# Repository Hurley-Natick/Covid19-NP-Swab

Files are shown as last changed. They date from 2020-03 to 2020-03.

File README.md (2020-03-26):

*Last updated: March 26, 2020 1600 ET*

# Making NP swabs

As clinical laboratories around the world have begun testing for Covid-19, we have encountered a new crisis: a shortage of the swabs required to obtain the necessary sample. These are called nasopharyngeal swabs, or NP swabs for short.

**The goal of this repository is sharing [methods](#design), [testing procedures](#testing), and [results](#results) required to manufacture NP swabs locally/everywhere at volumes of thousands per day, until standard manufacturers can make and deliver more.**

Because the crisis is **now,** the goal is to re-create versions of the swabs already in use (as opposed to creating better/fundamentally different redesigns).

The files in this repo contain some information to get started. **This includes .stl files that you can modify/print (see [design_files](design_files/) above).**

If anyone has any questions, please reach out to any of the contributors here or to Dr. Ramy Arnaout, MD, DPhil, at rarnaout@bidmc.harvard.edu.

Anything you find here is free for use for all.

If you want us to test swab materials at BIDMC we are happy to, please contact Cody Callahan at BIDMC (ccallah4@bidmc.harvard.edu).

For efficiency, we strongly suggest you find local partners either in addition or instead for [testing](#testing) and ask one of [us](#contact) for write access to share your [results](#results) here on the repo.

## Summary, March 25, 2 p.m. ET

Please see [here](Results/README.md).

## Contents

- [Basic description of an NP swab](#design)
- [Requirements](#reqs)
- [Anti-requirements: What's not required](#not-reqs)
- [List of known acceptable swabs](#acceptable-swabs)
- [Manufacturing approaches](#approaches)
- [Flock](#flock)
- [Materials and adhesives](#adhesive)
- [Packaging](#packaging)
- [Testing procedures](#testing)
- [Results](#results)
- [Contact](#contact)

## Basic description of an NP swab

(Click images for larger versions)





An NP swab is a flexible stick around 15cm in length that goes up your nose to the back of the nasal cavity (see [movie](https://www.youtube.com/watch?v=hXohAo1d6tk&feature=youtu.be&t=40)). It is swept or twirled around to brush or wick up secretions, which carry Covid-19 virus particles. The swab comes out of the nose and goes into a vial that contains fluid (viral transport medium, VTM, for which there are now recipes [from IU](Other_Docs/VTM_IU_recipe.pdf) and [the CDC](Other_Docs/CDC_Viral-Transport-Medium.pdf)). The vial gets capped and sent for processing.

There are **two parts**: a bristled **bulb** end (above) and a **shaft**. The bristles in the above are nylon.

The bulb looks like it would be fluffy to the touch but it is not: the bristles are short enough that it feels more like hard foam.

Often the shaft itself has a thin **neck**, for flexibility, and a thicker **handle**. The handle is often **scored**---a weak point in the shaft---where you can break it off so the bristled part stays in the vial; the handle is then thrown away.

**Score at \~7 cm from bulb tip.** The location of the score (distance from the bulb along the handle) must be smaller than the height of the vial you use. For example, for the vials for use with Copan 480C swabs, the breakpoint is 7cm; for [15-](https://www.fishersci.com/shop/products/falcon-15ml-conical-centrifuge-tubes-5/p-193301) or [50-mL](https://www.fishersci.com/shop/products/falcon-50ml-conical-centrifuge-tubes-2/p-193321) conical tubes (of the kind used routinely in biomedical research and sold by many manufacturers), 11 cm will do. It is mildly easier for handling if the score is close to the height of the vial but the requirement is that it is less than the height.

Helpful target measurements:

- Diameter of head with bristles: 3mm
- Diameter of head without bristles: \~2mm
- Diameter of neck: 1mm
- Diameter of handle: 2.5mm
- Length of bulb: 15mm
- Length that will be submerged in [transport medium](#pcr): \~30mm

# Requirements

## Medical requirements

-	**Stiffness, flexibility.** Wand is stiff enough to push to the back of the nasal cavity but flexible enough to get up the nose and will bend when it hits resistance instead of stabbing people (for reference, swabs are a little more flexible than the tiny straws used for coffee, and somewhat similar to the inside tube that holds the ink when you take apart a Bic ballpoint pen). **Swab must not snap off in patient's nose**

-	**Tip.** Ideally, the bulb end is *flocked* (see below): it has lots of tiny bristles perpendicular to the wand (see close-up above). The bristles provide for a high surface-area-to-volume and helps both wick secretions onto the bristle and liberate particles when put in the transport medium. Perpendicularity is a nice-to-have that we believe may improve yield slightly but requires electrostatic deposition; even random orientation of flock should work fine

-	Bristles or collecting substrate (including any adhesive) must be firmly attached and not get left behind in the nasal cavity. Similarly no part of the swab should break off or get left in the nasal cavity

-	[Materials](#adhesive) cannot inhibit [PCR](https://en.wikipedia.org/wiki/Reverse_transcription_polymerase_chain_reaction). This means no wood or cotton (although we believe rayon is OK). Nylon and polypropylene seem to be good choices, but start with medical equipment/grade materials if possible since they should be high quality/pure (some additives can be inihibitors).

-	Wand must break off inside the tube – better to be too short than too long.  Wand could be manually scored to create a weak point. If not, might need scissors at point of care (not ideal)

For more technical requirements, see [Design Constraints](Other_Docs/Design%20Constraints.md)

## Anti-requirements: What's not required

-	Sterility. Not a major concern for most uses; only for immunocompromised (in which case the ability to decontaminate by [autoclaving](https://en.wikipedia.org/wiki/Autoclave) or ethanol or isopropanol bath is needed). The air and the nose are already non-sterile and the PCR assay is specific enough to ignore most contaminants (as long as other Covid-19 contaminated things/people don’t come in contact with it and it doesn’t pick up PCR inhibitors)

-	Labor intensive is ok, to fill short term needs. There are students and researchers out of school and lab who are willing to volunteer to hand-assemble these from inoculation loops, adhesive, and wicking substrate #studentArmy

## List of known acceptable swabs

Model what you make after one of these.

Product numbers are listed. Unless otherwise stated, these are from the [FDA approved list](https://www.fda.gov/medical-devices/emergency-situations-medical-devices/faqs-diagnostic-testing-sars-cov-2) current as of **March 20, 2020**. You can look these up online.

**Copan:** 480C *(2)*, 481C *(1)*, 482C *(1)*, 501CS01, 503CS01, 516CS01, 518CS01, 534CS01

**Puritan:** LA-117 *(1)*, 3317-H, 25-3317-H, 25-3316-U, 25-3316-H, 25-3317-U, 25-3318-U, 25-3318-H, 25-3319-H, 25-3320-U, 25-3320-U EMB 100MM, 25-3320-U EMB 80MM, 25-3320-H and 25-3320-H EMB 80MM

*(1)* Preferred, per FDA

*(2)* Acceptable, per BIDMC

## Manufacturing approaches

**We believe the best use of resources is to be creative around copying the template, not redesigning swabs.**

- 3D print a shaft, and attaching flock material via adhesive

- 3D print a shaft with enough definition---either "nubs" along the surface or bristles---to gather secretion from the nasopharynx.

For more detail on ideas not yet investigated, including repurposing unrelated items like cosmetics applicators, or using other items common in labs, see [Other Approaches](Other_Docs/Repurposing_Approach.md)

### 3D-print shaft + adhesive + swab

- 3D print a wand with the appropriate form factor (e.g. see the picture above and the .stl files)
- dip bulb in adhesive (we are working on appropriate adhesives)
- dip sticky bulb in [flock](#flock)
- shake/blow/rinse off excess flock
- (if needed) dip in 70% ethanol for sterilization

(This is like how you'd solve this problem if you were in elementary school.) Currently we have no proven way to automate the last three steps so we are envisioning a "student army." Better ideas welcome.

### 3D-print entire swab

The ability to print a swab complete with bristles or equivalent saves the steps for requiring adhesive and [flock](#flock).

Stereolithography 3D printed prototypes by **OPT Industries** look promising (see example bulbs, below---note in this approach the whole swab including bulb is printed at once, on their own DLP/SLA machines); we are testing materials now.

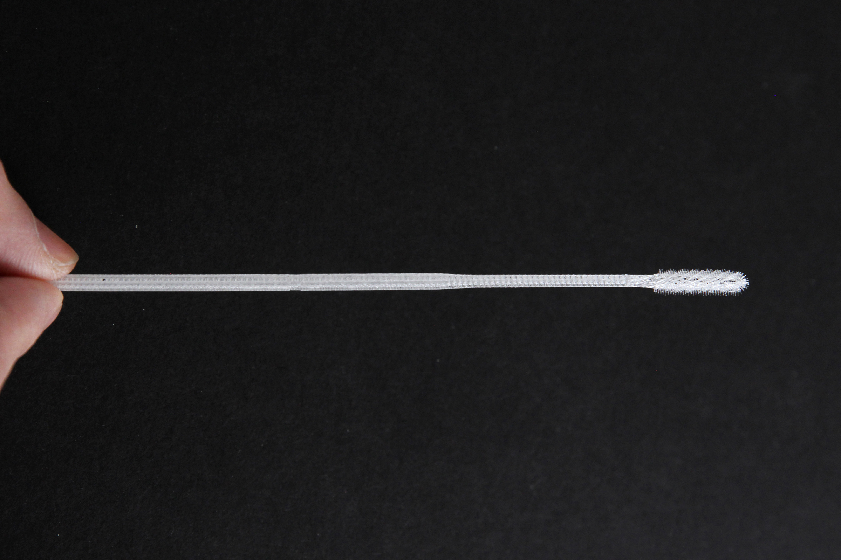
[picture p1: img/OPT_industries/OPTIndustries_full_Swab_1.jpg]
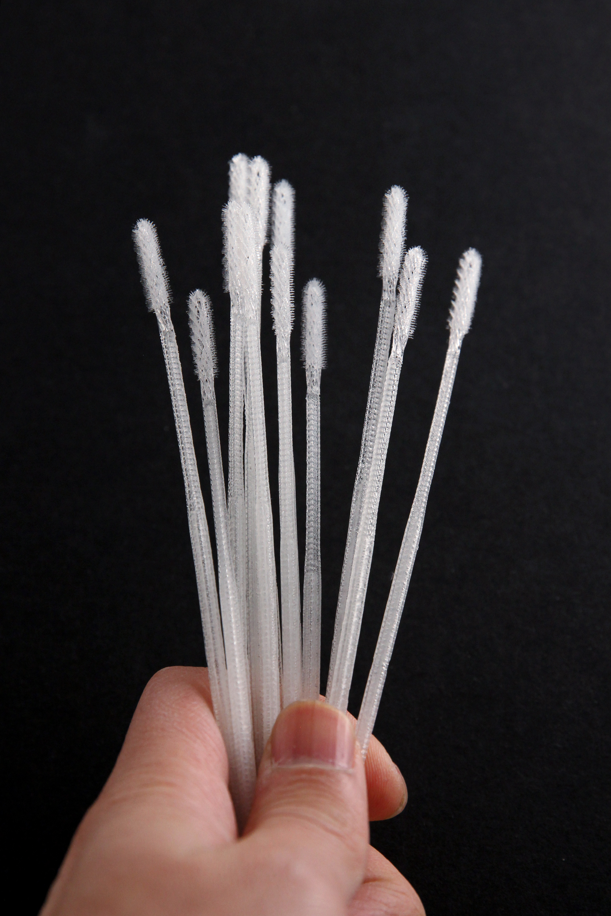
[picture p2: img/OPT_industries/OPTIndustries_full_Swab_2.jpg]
 

## Flock

"Flock" is the name of the bristle material. It can be ordered from e.g. www.flockit.com as a powder. The below information comes from extremely helpful conversations with them and Celluseude, the manufacturer.

- The nylon flock on the tip of the picture is 3 [denier](https://en.wikipedia.org/wiki/Units_of_textile_measurement#Denier) (3 [dtex](https://en.wikipedia.org/wiki/Units_of_textile_measurement#Denier))

- The flock on the flocked swab above was likely applied using electrostatic deposition: flock coated with something positively charged, shaft coated with adhesive and electrically grounded. We do not need to do this: the previous version of swabs, still widely in use, have matted flock and they work well enough (slightly lower sensitivity but clinically for now we'll take it)

- In general acrylic is used as the adhesive for flock, but be aware that acrylic is a **known PCR inhibitor** (see below). Decision point is rinse a lot to remove loose acrylic vs. just use something safer. Apparently Elmer's has something of the same problem.

- The only colors you should consider for the nylon are black and white, with preference for white. Black has some inorganic compound that is assumed to be PCR-safe; white has titanium inside the fiber but not on the surface so is more likely PCR safe. (White is the purest nylon.) Colored nylons have various ionic or covalent groups on the outside, which are unnecessary complications.

- Rayon is also safe to use

## Shaft

This is the easiest part to 3D-print.

It should be able to be easily broken off, so that only the tip with the patient's nasal secretion is in a specimen container.  Easy break-off may be accomplished via scoring.

## Packaging

As we get closer to having swabs, we will want a solution for packaging. Ideally at least semi-sterile, definitely single-swab packaging.

EnvisionTec has an FDA approved single-swab packaging system, that is capable of printing both the swab and container simultaneously.

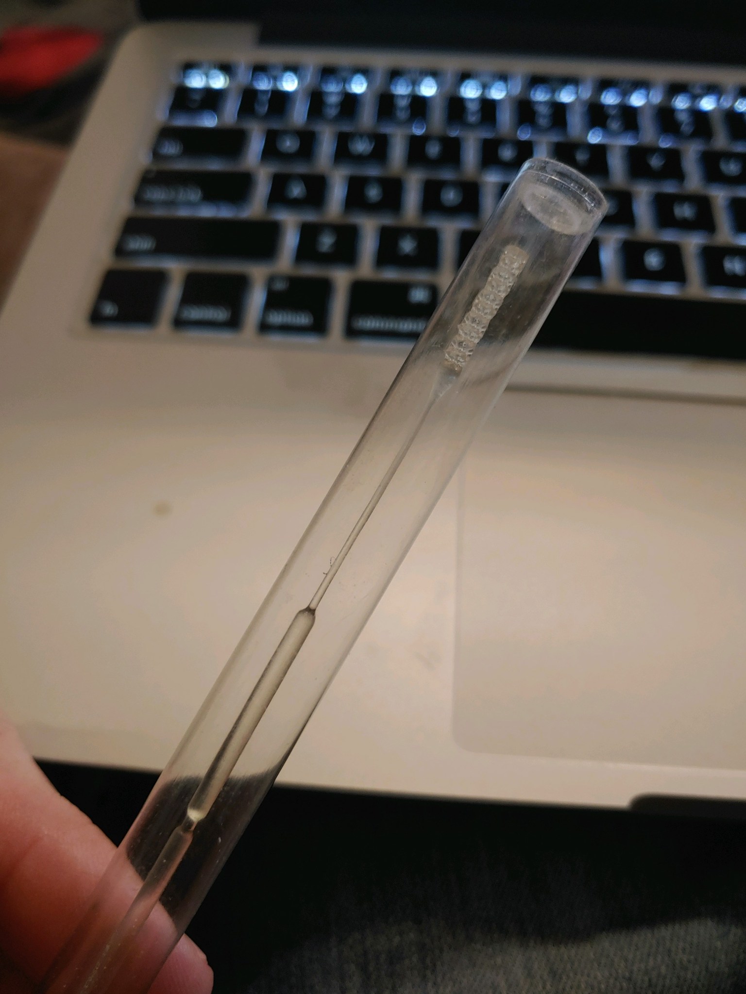
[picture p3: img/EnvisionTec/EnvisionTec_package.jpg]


Possibly will want to fork this process: more sterile for immunocompromised patients, less for others.

Current best thought is to package manually in sterile hoods:

- begin with swabs in ethanol vat/bucket
- spread and cut plastic wrap
- leave under UV light in hood (*1*)
- take swab out of ethanol and place horizontally on strip of plastic to dry
- **When dry,** fold plastic over swab
- packing done

(*1*) UV is not expected to destroy plastic on timescales of under a few hours

Thoughts on throughputting this?

## Materials and adhesives

Adhesives will need to adhere the two substances (printed shaft + flock) and will need to not leave behind anything in the nasal cavity / nasopharynx when used.

Some materials and adhesives inhibit PCR (see [testing protocol](#pcr) below). See the [Kodzius 2012](Other_Docs/kodzius2012.pdf) and [forensicGEM's work](Other_Docs/forensicGEM_Tissue_AppNote_TapeInhibition.pdf) for details.

From those files:

### Safe materials (any red bar above \~50 in [Kodzius Fig. 3](Other_Docs/kodzius2012.pdf)): (*1*)
- polypropylene
- PTFE
- PDMS
- SiO2 quartz
- Pyrex glass
- Soda-lime glass
- NOA68

### Unsafe materials:
- PMMA
- Silicon
- SiO2 5600A
- ITO glass
- SU-8
- NOA61

### Unknown:
- metals including steel and aluminum (in principle these stick to polymerase, but the effect size depends on the form factor so we don't know yet)
- polycryl resin (we believe the monomers are not PCR safe, but if cured and washed could be ok; we will test)

### Safe adhesives (from Kodzius Fig. 3 and from forensicGEM document Fig. 1):
- Wax (Tm 80C)
- the glue used in Scotch Magic Tape 810
- the glue used in Scotch Crystal Clear Tape
- the glue used in Scotch Mailing Tape
- the glue used in Scotch Storage Freezer Tape
- the glue used in Scotch Transparent Tape 550
- the glue used in Sellotape Brown Packaging Tape
- the glue used in Applied Biosystems MicroSeal Adhesive Film

### Unsafe adhesives:
- Wax (Tm <80C)
- Epoxy glue
- Acrylic glue
- the glue used in Scotch Masking Tape (made in Canada or Taiwan)
- the glue used in Scotch Removable Magic Tape 811
- the glue used in Sellotape Diamond Ultra Clear
- the glue used in Sellotape Invisible Permanent Write-on
- the glue used in Sellotape Cellulose Easy-Tear Tape
- the glue used in Sellotape Double-Sided Tape
- the glue used in 3M PostIt notes

(*1*) Some materials can in principle be used as adhesives, e.g. PDMS

## Testing procedures

We propose/are using a three-step testing procedure:

- expert review
- sufficient collection of material
- PCR compatibility

### Expert review

There is no substitute for having a health professional who actively uses NP swabs evaluate your prototype. If such an expert says it "looks good," that is enough to pass this test (see [Results](#results) below)

Two frequently-asked questions are re: length and flexibility. For length, our current recommendation is 15cm. For flexibility: if you have a [swab to compare to](#acceptable-swabs), that is the best way to guage flexibility. If not: your swab should as flexible as the inside part of a standard Bic ball-point pen (the tube that contains the actual ink, when you take the pen apart).

### Sufficient collection of material

For collection of material:

- swirl against the inside of your cheek (make sure the swab is clean first)
- rub on a slide
- perform a [Gram stain](https://en.wikipedia.org/wiki/Gram_stain)
- visualize under a microscope
- take picture through ocular
- compare picture to control we made using an actual NP swab (to be posted soon)

The viral particles we are looking to collect are smaller than bacteria, but if you collect a fair number of bacteria, that is considered Ok for now (ask a microbiologist or microbiology tech, and we will provide a picture of what we think is acceptable when we can).

### PCR compatibility

It is essential to confirm that nothing in the final product (material ± adhesive) inhibits RT-PCR, on which current tests are based (details of the reagents differ somewhat from assay to assay; we will post). A testing protocol is as follows. Note because this has a substantial incubation time, **it is a good idea to start testing materials before prototypes are done, if possible.**

- incubate bulb in 3mL Viral Transport Medium (VTM; [recipe courtesy IU](Other_Docs/VTM_IU_recipe.pdf)) overnight (12 hr)
- spike the VTM with positive control (*1*)
- aliquot 700µl for testing
- run RT-PCR (*2*) (*3*)

(*1*) If you are working with clinical labs who have the bandwidth, they can use inactivated Covid-19 particles that are used clinically as the positive control any virus. If not, and you are/have access to colleagues in a virology lab working with encapsulated virus, that can be used. If not, then any mRNA.

(*2*) Many protocols and reagents are proprietary, but many hospitals have developed their own laboratory-developed tests (LDTs) that may have made their protocols publicly available. If you find and [forward](#contact) we will post.

(*3*) An RNA extraction step [may not be required](https://www.biorxiv.org/content/10.1101/2020.03.20.001008v1)

See also [this FDA page](https://www.fda.gov/medical-devices/emergency-situations-medical-devices/faqs-diagnostic-testing-sars-cov-2) for speific testing details.

## Results

As materials and designs (including existing swabs) get tested, we will record passing results [here](Results/np_swab_results.xlsx) (as opposed to screenshots). See images in the appropriate subfolders in the [img/ directory.](img/)

Please organize entries into the following fields. We plan to turn into a (sortable, updatable) table, but don't wait for that: just upload entries (separating each entry by line breaks). Please **copy** the below for each entry (i.e., don't overwrite it). If you need help [contact us](#contact).
___

### ENTRY TEMPLATE

#### Identifier
This is a unique identifier, ideally including the source's name

#### Date of test

#### Test site
E.g., BIDMC

#### Picture
Please take a high-resolution picture of the **entire** item provided.

#### Material
Please describe all (known) materials in the bulb head, including plastic, any adhesive, and any flock

#### Process
Please include a brief description of the design process that an expert would understand well enough to reproduce. For repurposed swabs, write "commercial."

#### Creator (contact info and company)
How to contact the creator for questions/further development

#### Link to stl and cad files
Please send .stl and CAD files, which we will post.

#### Test 1: NP swab user evaluation (eg an ID doc), with comments
If passes, write "Pass". If fails, write "Fail" and give a brief reason why. Should be filled out by someone who has experience actually using NP swabs in a clinical context. Please leave the name of this person.

#### Test 2: Collection test
If a Gram stain of the (inner) cheek made from the swab shows material broadly consistent with our control, then write "Pass". If not, "Fail" and give reason (too abrasive, did not pick up material, etc.) NOTE: BIDMC is not using fluid in Gram stain.

#### Test 3: PCR compatibility (and which protocol used)
As above, "Pass" vs. "Fail". Please indicate the protocol used. You can post the protocol in the Testing/ directory, and link to it here

___

#### Identifier
This is a unique identifier, ideally including the source's name

#### Date of test

#### Test site
E.g., BIDMC

#### Picture
Please take a high-resolution picture of the **entire** item provided.

#### Material
Please describe all (known) materials in the bulb head, including plastic, any adhesive, and any flock

#### Process
Please include a brief description of the design process that an expert would understand well enough to reproduce. For repurposed swabs, write "commercial."

#### Creator (contact info and company)
How to contact the creator for questions/further development

#### Link to stl and cad files
Please send .stl and CAD files, which we will post.

#### Test 1: NP swab user evaluation (eg an ID doc), with comments
If passes, write "Pass". If fails, write "Fail" and give a brief reason why. Should be filled out by someone who has experience actually using NP swabs in a clinical context. Please leave the name of this person.

#### Test 2: Collection test
If a Gram stain of the (inner) cheek made from the swab shows material broadly consistent with our control, then write "Pass". If not, "Fail" and give reason (too abrasive, did not pick up material, etc.)

#### Test 3: PCR compatibility (and which protocol used)
As above, "Pass" vs. "Fail". Please indicate the protocol used. You can post the protocol in the Testing/ directory, and link to it here

___

## Contact us

We want to emphasize this is a **group effort** with literally scores of people working on this right now; if you're reading this, you're probably one of them. If you have something to contribute, please contact Dr. Ramy Arnaout, MD, DPhil, at rarnaout@bidmc.harvard.edu.

Note there's also now a [Slack channel](https://join.slack.com/t/rapidmanufact-iop4498/shared_invite/zt-cykndes6-XtxzG~8bkji64M3wTVWiOw).

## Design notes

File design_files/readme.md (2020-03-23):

# Please upload and download models here

## USF Models
- Dr. Summer Decker (sdecker@usf.edu)
- Jonathon Ford (jmford2@usf.edu )
- designed for formlabs surgical material; can autoclave; clinician tested; awaiting virology test
- being tested in MJF

1) 

## Fathom Models
- Anne Pauley (anne@studiofathom.com)
- Chris Blower (cblower@studiofathom.com)
- Tony Slavik (tony@studiofathom.com)
- Sldparts / Step / Stl files;
- designed to wick/retain fluid for capillary action, surface tension

1) 
2)
3)

## OPT Industries Models
- Jifei Ou (jifei@optindustries.com)
- stl too big to upload to GitHub. dropbox link below
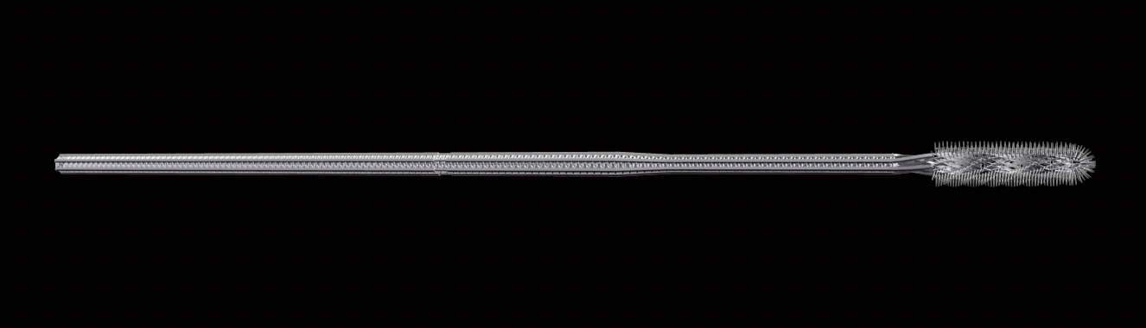
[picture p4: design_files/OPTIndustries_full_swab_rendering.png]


https://www.dropbox.com/s/ce44jchs8vurto6/OPTIndustries_Swab_CilliaReinforced.stl?dl=0

## Abiogenix Models
- Goutam Reddy (greddy@abiogenix.com)
- Fusion 360 links to CAD models

1) nasopharyngeal swab nubs V1:  https://a360.co/2Qyh2GE
   - 
   - bristle with 6x15 0.7mm dia raised nubs,
   - bristle surface area 129 mm^2
   - need to fix shaft so max-stress point is at snap-off point, not on bristle shaft
    
2) nasopharyngeal swab round V1:  https://a360.co/2wpGHui
   - 
   - featureless bristle: 1.25mm diameter shaft
   - bristle surface area: 61 mm^2
   - LESS SURFACE AREA BUT CAN BE USED TO ATTACH EXTERNAL BRISTLE OR COATING
   
3) nasopharyngeal swab nubs holes V1: https://a360.co/2U5CzbK
   - 
   - bristle with 6x15 0.7mm dia raised nubs, and 0.35mm dia holes
   - bristle surface area: 167 mm^2
   - PREFER NOT TO USE MODELS WITH HOLES INSIDE TO REDUCE POST-PROCESSING

## Wyss Institute Models
- *find author contact info*
- *find link to original model files*
1) nasopharyngeal swab helix: *find link to model*
2) nasopharyngeal swab linear balls: *find link to model*

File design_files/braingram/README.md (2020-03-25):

Inspired by Jenny's DIYSwab design this should be printable on any FDM that
can print a suitable material (perhaps nylon or PP). The process uses the
[3D printing on fabric](https://www.instructables.com/id/How-to-3D-Print-Onto-Fabric/)
technique to embed mesh inside a 3D printed swab.

The construction process involves:

1. printing a base layer for all swabs
1. while the printer is paused, placing the mesh onto the print surface (taped to the bed to keep it in place)
1. finishing the print, traping the mesh between the layers
1. letting the parts cool before removing them from the build plate
1. cutting away the excess mesh

For the v1 prototype, 5 swabs were printed in 6 minutes (not including heat-up/cool-down).
Dimensions were guessed (100 mm long shank, 50 mm break-off, ~4x2 mm inside loop).

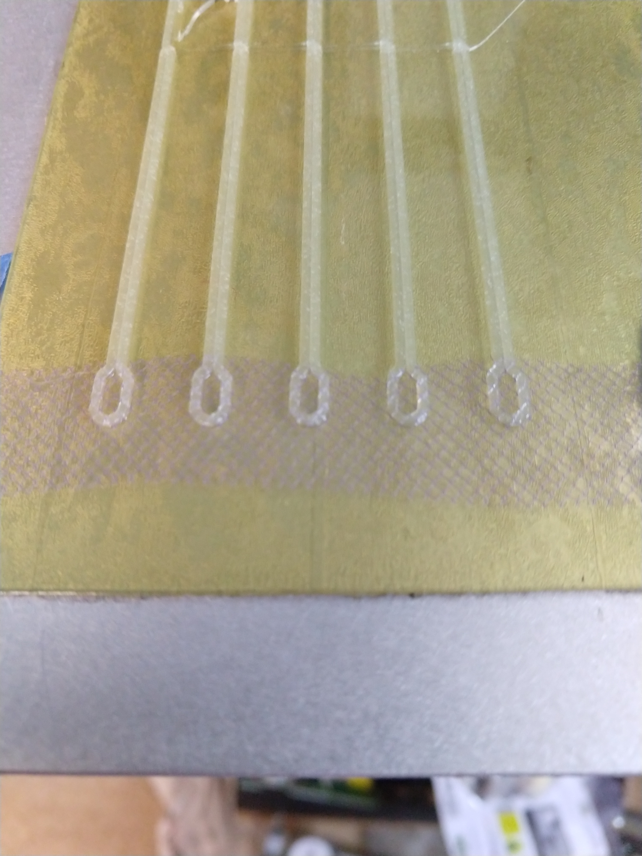
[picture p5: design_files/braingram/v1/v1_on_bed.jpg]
parts on bed

overview
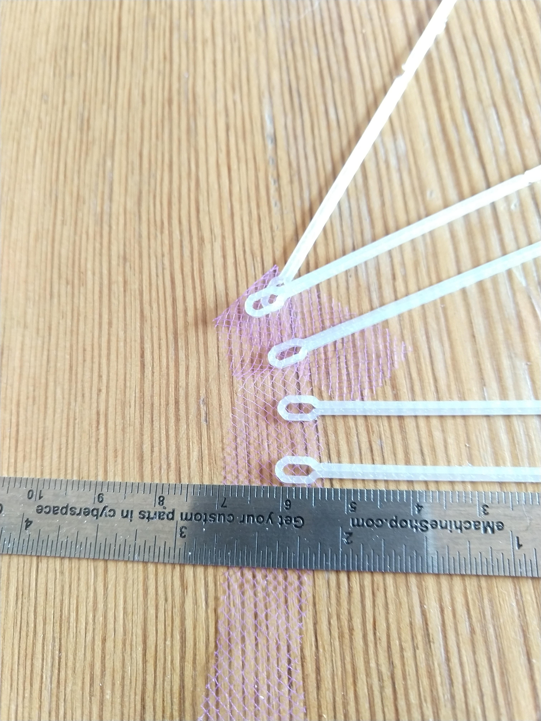
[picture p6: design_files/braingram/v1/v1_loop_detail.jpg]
loop detail

break point
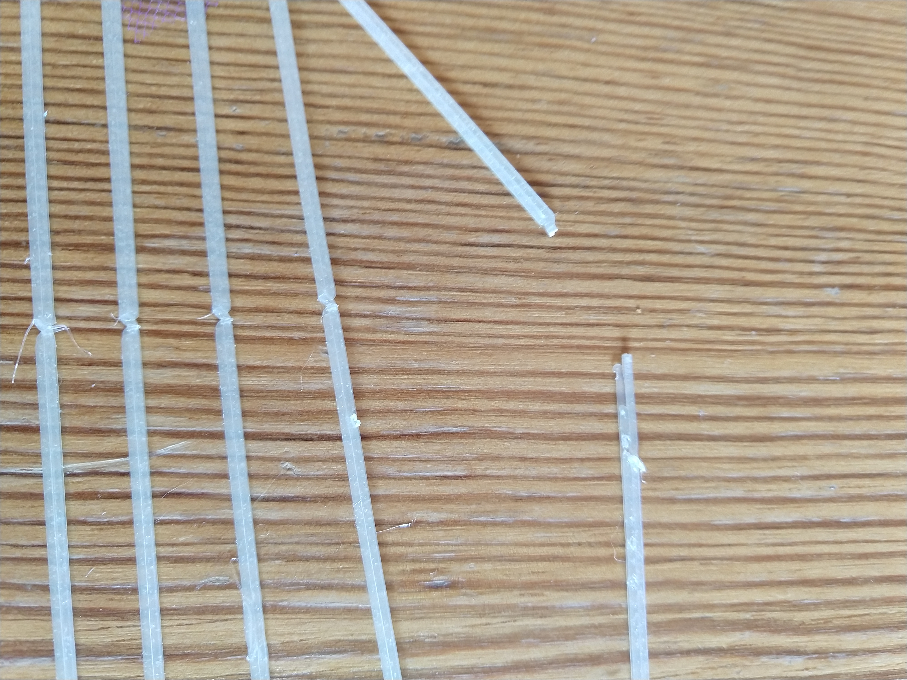
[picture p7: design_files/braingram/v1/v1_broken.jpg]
broken swab


Although the included [code](v1/gen_swab_gcode.py) generates gcode directly
the design could likely be made compatible with a standard slicer to improve
print quality by using retracts etc.

___

#### Identifier
BGV1Swab

#### Date of test
None

#### Test site
None

#### Picture
Please take a high-resolution picture of the **entire** item provided.

#### Material
Initial prototype in PLA and unknown mesh (only material on hand).

#### Process
Please include a brief description of the design process that an expert would understand well enough to reproduce. For repurposed swabs, write "commercial."

#### Creator (contact info and company)
Brett Graham brettgraham@gmail.com

#### Link to stl and cad files
Please send .stl and CAD files, which we will post.

#### Test 1: NP swab user evaluation (eg an ID doc), with comments
None

#### Test 2: Collection test
None

#### Test 3: PCR compatibility (and which protocol used)
None

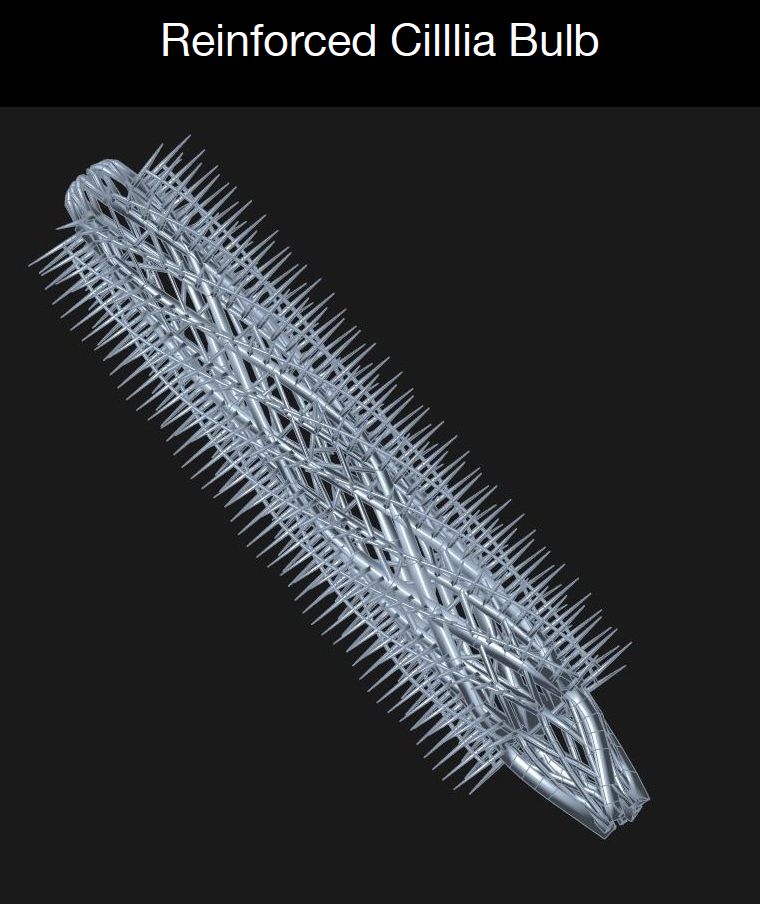
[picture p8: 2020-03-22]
img/OPTIndustries_full_Swab_design.png

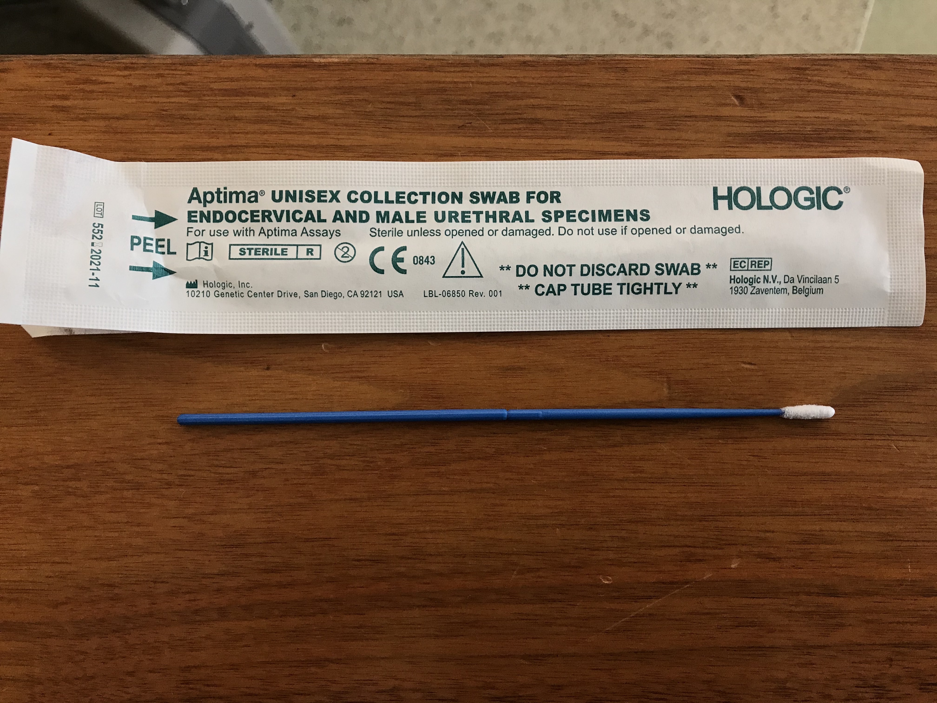
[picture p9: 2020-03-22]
img/Aptima/aptima_unisex_collection_swab_for_endocervical_and_male_urethral_specimena.JPG

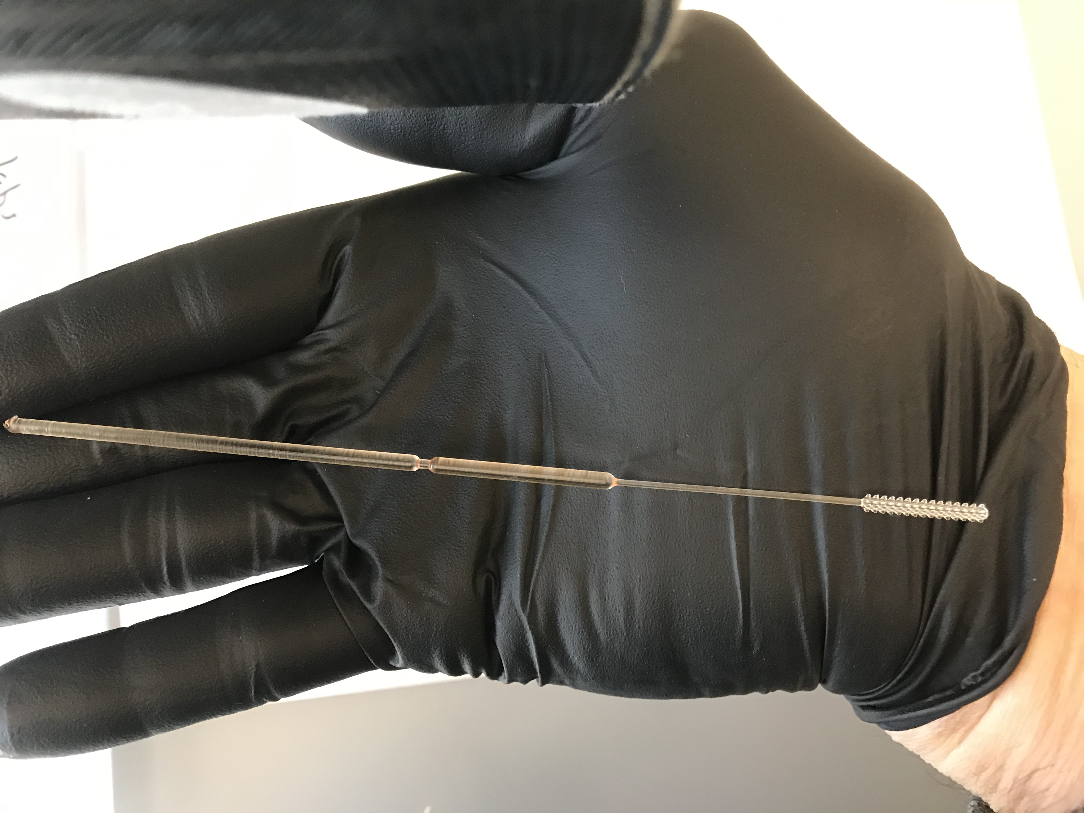
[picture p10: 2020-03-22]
img/FormLabs/form_labs.JPG

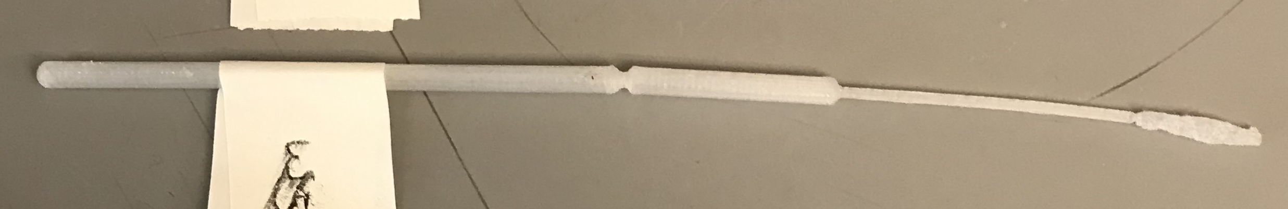
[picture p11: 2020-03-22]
img/Wyss/wyss_w5.png

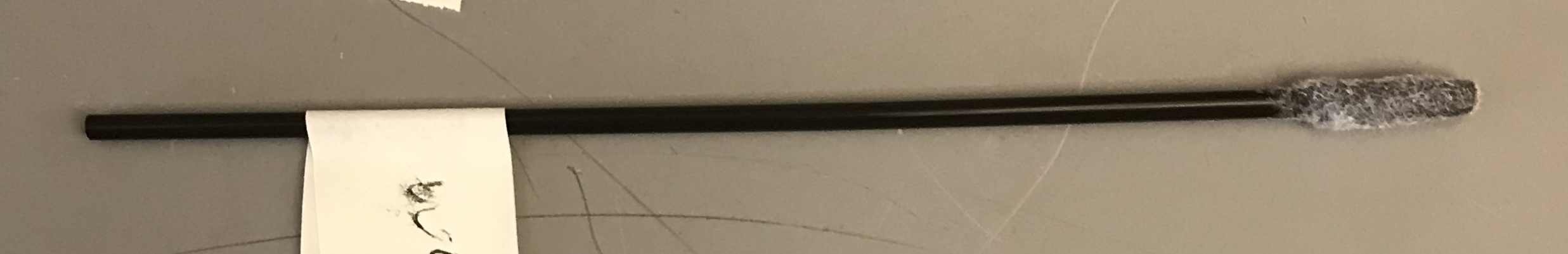
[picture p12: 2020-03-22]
img/Wyss/wyss_w4.png

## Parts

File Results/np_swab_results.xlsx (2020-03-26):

ID | Description | Date of test | Test site | Picture | Material | Process | Creator (contact info and company) | Link to stl and cad files | Test 1: Expert evaluation | Test 2: Collection sufficiency | Test 3: PCR compatibility | Notes
This is a unique identifier, ideally including the source's name |  |  | E.g., BIDMC | Please take a high-resolution picture of the entire item provided. | Please describe all (known) materials in the bulb head, including plastic, any adhesive, and any flock | Please include a brief description of the design process that an expert would understand well enough to reproduce. For repurposed swabs, write "commercial." | How to contact the creator for questions/further development | Please send .stl and CAD files, which we will post. | If passes, write "Pass". If fails, write "Fail" and give a brief reason why. Should be filled out by someone who has experience actually using NP swabs in a clinical context. Please leave the name of this person. | If a Gram stain of the (inner) cheek made from the swab shows material broadly consistent with our control, then write "Pass". If not, "Fail" and give reason (too abrasive, did not pick up material, etc.) Note: BIDMC protocol does not include adding fluid. | As above, "Pass" vs. "Fail". Please indicate the protocol used. You can post the protocol in the Testing/ directory, and link to it here
Puritan Sterile polyester-tipped applicators 25-806 1PD |  | 2020-03-22 | BIDMC | img/Puritan/puritan_sterile_polyester_tipped_applicator_25-805_1PD.png | Polyester tip | Commercial | Puritan | NA | Did not pass (tip diameter too large) | Not done
Fisher polyester-tipped applicators 22363164 |  | 2020-03-22 | BIDMC | img/Fisher/fisher_polyester_tipped_applicators_22363164.png | Polyester tip | Commercial | Fisher | NA | Did not pass (tip diameter too large) | Not done
Puritan sterile foam tipped applicator 25-1506 1PF |  | 2020-03-22 | BIDMC | img/Puritan/puritan_sterile_foam_tipped_applicator_25-1506_1PF.png |  | Commercial | Fisher | NA | Pass (but tip diameter large, would be difficult to use) | Pass | Pass
Copan BD ESwab collection and transport system 220532 |  | 2020-03-22 | BIDMC | img/Copan_BD/copan_BD_ESwab_collection_and_transport_system_220532.png |  | Commercial | Fisher | NA | Pass | Pass
Copan ESwab 220245 |  | 2020-03-22 | BIDMC | NA |  | Commercial | Fisher | NA |  |  | Pass
Hologic Aptima LBL-06850 |  | 2020-03-22 | BIDMC | Pending |  | Commercial | Fisher | NA | Pass (but tip diameter large) |  | Pass
Jifei "Carbon" (internal ID, *not* Carbon3D the company) |  | 2020-03-22 | BIDMC | (meth)acrylated urethane photopolymer |  |  | OPT Industries (Jifei Ou) |  |  | Pass | Pass
Jifei Material 2 |  | 2020-03-22 | BIDMC | (meth)acrylated urethane photopolymer | Material 2 |  | OPT Industries (Jifei Ou) |  | NOT SWAB MATERIAL ONLY | NOT SWAB MATERIAL ONLY | Pass
Nilson |  | Mach 20,2020 | BIDMC |  | Rose-print1 | Printed usign E Guide 2.0, cleaned in 99% IPA, 2000 Flash cure with ottoflash unit |  |  |  |  | Pass
Formlabs - Honey Tip |  | 2020-03-22 | BIDMC | img/FormLabs/honeydipper.png |  |  | FormLabs (Craig Brody) |  | Did not pass (shaft needs to be smooth; material too brittle) | Pass | Pass
Formlabs - Spiral Tip |  | 2020-03-22 | BIDMC | Formlabs Surgical Guide img/FormLabs/surgical_guide_technical_data_sheet_en.pdf |  |  | FormLabs (Craig Brody) |  | Did not pass (shaft needs to be smooth; material too brittle) | Did not pass (material did not transfer to slide?) | Pass
Formlabs - Bristle Tip |  | 2020-03-22 | BIDMC | img/FormLabs/bristles.png |  |  | FormLabs (Craig Brody) |  | Did not pass (shaft needs to be smooth; material too brittle) | Did not pass (material did not transfer to slide?) | Pass
Formlabs - Dental LT clear (Bristle, Honey tips) |  | 2020-03-22 | BIDMC | img/FormLabs/DentalLT.jpg |  |  | FormLabs (Craig Brody) |  | Did not pass (tip needs to be more flexible - will abutt posterior nasopharynx, but flexibility of NP neck, handle/body still needs to be more smooth)
Formlabs - Dental SG (Fern tip) |  | 2020-03-22 | BIDMC | img/FormLabs/SG.jpg |  |  | FormLabs (Craig Brody) |  | Did not pass (tip needs to be more flexible - will abutt posterior nasopharynx, but flexibility of NP neck, handle/body still needs to be more smooth) | Pass
Formlabs - Grey Pro (Spiral, Honey, Bristle) |  | 2020-03-22 | BIDMC | img/FormLabs/GreyPro.jpg |  |  | FormLabs (Craig Brody) |  | Did not pass (material brittle, tip needs to be more flexible - will abutt posterior nasopharynx, but flexibility of NP neck, handle/body still needs to be more smooth)
Formlabs - Durable (Fern, Honey, Bristle) |  | 2020-03-22 | BIDMC | img/FormLabs/Durable.jpg |  |  | FormLabs (Craig Brody) |  | Did Not Pass (Flexibility of tip appropriate, but neck for these designs is too elastic, difficult to pass middle turbinate, and folds in external nasal cavity) | Pass (All but Bristle tip -very few cells with that tip) | Pass | *Tested this material as was closest to desirable design although did not pass Test 1
Formlabs Tough (Spiral, Bristle, Honey, Fern) |  | 2020-03-23 | BIDMC | img/FormLabs/tough.jpg |  |  | FormLabs (Craig Brody) |  | Did not pass (tip needs to be more flexible - will abutt posterior nasopharynx)
Formlabs Dental Model (Honey, Bristle) |  | 2020-03-24 | BIDMC | img/FormLabs/model.jpg |  |  | FormLabs (Craig Brody) |  | Did not pass (tip needs to be more flexible - will abutt posterior nasopharynx, and material too brittle)
Formlabs Tough 1500 (Spiral, Brittle) |  | 2020-03-25 | BIDMC | img/FormLabs/tough1500.jpg |  |  | FormLabs (Craig Brody) |  | Did not pass (tip needs to be more flexible - will abutt posterior nasopharynx)
Formlabs Tough - Tip 4 (Spiral, Bristle, Honey, Fern) |  | 2020-03-26 | BIDMC | img/FormLabs/tough.jpg |  |  | FormLabs (Craig Brody) |  | Did not pass (tip needs to be more flexible - will abutt posterior nasopharynx)
Harvard Army |  | 2020-03-22 | BIDMC | img/Harvard_army/new_skin.png |  |  | Army (Kit Parker) |  | Did not pass (material too brittle) | "New Skin" passes; others did not pass (too little material) |  | (3 glues used - Locktite, Dermabond, New skin)
Harvard Army Ultem |  | 2020-03-23 |  | img/Harvard_army/ultem.jpg |  |  | Army (Kit Parker) |  | Did not pass (material too brittle, tip inflexible
Harvard Army Onyx |  | 2020-03-23 |  | img/Harvard_army/onyx.jpg |  |  | Army (Kit Parker) |  | Did not pass (tip too inflexible)
Harvard Army Polyjet |  | 2020-03-23 |  |  |  |  | Army (Kit Parker) |  | Pass | (not tested, only one swab which was tested for PCR) | Pass
W1 |  | 2020-03-22 | BIDMC | img/Wyss/wyss_w1.png | rayon, fiber, silicon glue, polycarbonate probe |  | Wyss Institute (Adama Sesay) |  | Pass | Pass
W2 |  | 2020-03-22 | BIDMC | img/Wyss/wyss_w2.png | nylon fiber (0.75µm), silicon glue, polycarbonate probe |  | Wyss Institute (Adama Sesay) |  | Did not pass (needs a tapered, flexible end) | Did not pass (No visible cells or bacteria)
W3 |  | 2020-03-22 | BIDMC | img/Wyss/wyss_w3.png | rayon fiber, silicon glue, nylon probe |  | Wyss Institute (Adama Sesay) |  | Pass | Did not pass (very few cells/bacteria)
W4 |  | 2020-03-22 | BIDMC | img/Wyss/wyss_w4.png | rayon immfiber, silicon glue, commercial straw |  | Wyss Institute (Adama Sesay) |  | Did not pass (needs a tapered, flexible end) | Pass
W5 |  | 2020-03-22 | BIDMC | img/Wyss/wyss_w5.png | nylon fiber (0.75µm), nylon probe, silicon glue |  | Wyss Institute (Adama Sesay) |  | Pass | Pass
W6 |  | 2020-03-22 | BIDMC | img/Wyss/wyss_w6.png | polycarbonate 3D-printed probe |  | Wyss Institute (Adama Sesay) |  | Pass | Pass
W7 |  | 2020-03-22 | BIDMC | img/Wyss/wyss_w7.png | nylon 3D-printed probe |  | Wyss Institute (Adama Sesay) |  | Pass | Pass
W8 |  | 2020-03-22 | BIDMC | img/Wyss/wyss_w8.png | nylon fiber (0.75µm), silicon glue, polycarbonate probe |  | Wyss Institute (Adama Sesay) |  | Pass | Pass
VWR 1ul loop + pellon p45 fabric knot - Jenny |  | 2020-03-22 | HH (Seattle) | https://github.com/HMS-RIC/Covid19-NP-Swab/tree/master/img/Jenny/DIYswab | polystyrene loop and pellon P45 fabric | see https://github.com/HMS-RIC/Covid19-NP-Swab/wiki/DIY-swab-assembly | Jenny |  | Pass (doctor/swabber was able to use 5mm loop, newer iteration is <3mm) - Jenny | need review of smear pics
USF_1_1 | Rings w/ medium spacing distance | 2020-03-23 | BIDMC | img/USF/USF1-1.jpg |  |  | HP (Rick Fulop; ricfulop@desktopmetal.com) |  | Did not pass (tip is too sharp but appropriately flexible, but body design (flexibility of neck and stiffness of handle is appropriate). There is a fine powder on these materials that we are concerned could be health hazard if aspirated | Pass | Pass
USF_1_2 | Rings w/ low spacing distance |  |  | img/USF/USF1-2.jpg |  |  | HP (Rick Fulop; ricfulop@desktopmetal.com) |  | Did not pass (tip is too sharp but stiff/brittle, but body design (flexibility of neck and stiffness of handle is appropriate). There is a fine powder on these materials that we are concerned could be health hazard if aspirated | Pass
USF_1_3 | Rounded tip w/ protrusions |  |  | img/USF/USF1-3.jpg |  |  | HP (Rick Fulop; ricfulop@desktopmetal.com) |  | Did not pass (tip is too sharp and stiff, but body design (flexibility of neck and stiffness of handle is appropriate). There is a fine powder on these materials that we are concerned could be health hazard if aspirated | Pass
USF_1_4 | Screw; finely threaded |  |  | img/USF/USF1-4.jpg |  |  | HP (Rick Fulop; ricfulop@desktopmetal.com) |  | Did not pass (tip is too sharp and stiff/brittle, but body design (flexibility of neck and stiffness of handle is appropriate). There is a fine powder on these materials that we are concerned could be health hazard if aspirated | Pass
USF_1_5 | Screw; medium thread |  |  | img/USF/USF1-5.jpg |  |  | HP (Rick Fulop; ricfulop@desktopmetal.com) |  | Did not pass (tip is too sharp but we like the spring and how flexible it is, but body design (flexibility of neck and stiffness of handle is appropriate). There is a fine powder on these materials that we are concerned could be health hazard if aspirated | Pass
USF_1_6 | Screw;large thread | 2020-03-23 |  | img/USF/USF1-6.jpg |  |  | HP (Rick Fulop; ricfulop@desktopmetal.com) |  | Did not pass (tip is too sharp but we like the spring and how flexible it is, but body design (flexibility of neck and stiffness of handle is appropriate). There is a fine powder on these materials that we are concerned could be health hazard if aspirated | Pass
HP_H | HP swabs with holes | March 23,2020 | BIDMC | img/HP/HPH.jpg |  |  | HP (LihuA Zhao; Zhao, Lihua <lihua.zhao@hp.com) |  | **Conflicting Results** Pass per Jenny Hu 032320: doctor swabber would like the shaft to be longer but likes the shaft flexibility and tip size. Not pass per BIDMC: tip not very flexible and too sharp at the end | **Conflicting Results** Pass per Jenny Hu 032320 (collected a few cells/bacteria from cheek swab then rubbing directly on slides; better results from rinsing the tip with 150ul of buffer then transfering liquid to slide). Not pass per BIDMC protocol (no elution); very few cells collected |  | Doing some more mechanical measurements/testing this afternoon then my doctor friend will stop by after work and I'll do NP swabs with Copan, HP_H, HP_NH, VWRloop+facric. Will smear swabs directly on slides then try rinsing and looking at rinse liquid for cells/bacteria.
HP_NH | HP swabs without holes | 2020-03-23 | BIDMC | img/HP/HPNP.jpg |  |  | HP (LihuA Zhao; Zhao, Lihua <lihua.zhao@hp.com) |  | **Conflicting Results** Pass per Jenny Hu 032320: doctor swabber would like the shaft to be longer but likes the shaft flexibility and tip size. Not pass per BIDMC: tip not very flexible and too sharp at the end | **Conflicting Results** Pass per Jenny Hu 032320 (collected a few cells/bacteria from cheek swab then rubbing directly on slides; better results from rinsing the tip with 150ul of buffer then transfering liquid to slide). Not pass per BIDMC protocol (no elution); very few cells collected | Pass | passed
C_1 | Carbon 3D bag 1 | 2020-03-23 | BIDMC | img/Carbon/C1.jpg |  |  | Carbon 3D ( Hardik Kabaria <hardik@carbon3d.com) |  | Pass (good stiffness of handle, and flexible tip), tapered more flexible neck would be better | Pass | Pass
C_2 | Carbon 3D bag 2 | 2020-03-23 | BIDMC | img/Carbon/C2.jpg |  |  | Carbon 3D ( Hardik Kabaria <hardik@carbon3d.com) |  | Pass (good stiffness of material, and flexible tip), tapered more flexible neck would be better | Pass
P_0 | Swab_test_Wyss | 2020-03-23 | BIDMC | img/Gorelik/P0.jpg | PA12 |  | Empire Group. (Pavel Gorelik; oreshki@gmail.com ) |  | Did not pass - tip needs to be more flexible, but stiffness of neck and elasticity of material appropriate)
P_1 | Solid_Circular | 2020-03-23 | BIDMC | img/Gorelik/P1.jpg | PA12 |  | Empire Group. (Pavel Gorelik; oreshki@gmail.com ) |  | Pass (tip more appropriately flexible, but would make tip end less jagged)
P_2 | Spring_Circular | 2020-03-23 | BIDMC | img/Gorelik/P2.jpg | PA12 |  | Empire Group. (Pavel Gorelik; oreshki@gmail.com ) |  | Pass (tip more appropriately flexible, but would make tip end less jagged) | Pass | Pass
P_3 | Spring_Flat | 2020-03-23 | BIDMC | img/Gorelik/P3.jpg | PA12 |  | Empire Group. (Pavel Gorelik; oreshki@gmail.com ) |  | Did not pass - tip needs to be more flexible, but stiffness of neck and elasticity of material appropriate) | Pass
P_4 | Solid_Flat | 2020-03-23 | BIDMC | img/Gorelik/P4.jpg | PA12 |  | Empire Group. (Pavel Gorelik; oreshki@gmail.com ) |  | Pass (tip more appropriately flexible, but would make tip end less jagged)
P_5 | Swab_Concentric | 2020-03-23 | BIDMC | img/Gorelik/P5.jpg | PA12 |  | Empire Group. (Pavel Gorelik; oreshki@gmail.com ) |  | Pass (tip more appropriately flexible, but would make tip end less jagged) | Pass
P_6 | Swab_concentric_bigger_pitch | 2020-03-23 | BIDMC | img/Gorelik/P6.jpg | PA12 |  | Empire Group. (Pavel Gorelik; oreshki@gmail.com ) |  | Pass (tip more appropriately flexible, but would make tip end less jagged) | Pass
P_7 | Swab_test_head_4_wyss | 2020-03-23 | BIDMC | img/Gorelik/P7.jpg | PA12 |  | Empire Group. (Pavel Gorelik; oreshki@gmail.com ) |  | Pass for tip head
J_1 | flexible swab w/ case | March 24th, 2020 | BIDMC | img/OPT_industries/J_1.jpg | methylacrylic urethane |  | opticalindustries, jifei jifei@optindustries.com |  | Pass but design too short | Pass | passed
USF_2_1 | swab w/ fine nubs | March 24th, 2020 | BIDMC | img/USF/USF_2_1.jpg |  |  | HP (Rick Fulop; ricfulop@desktopmetal.com) |  | Did not pass (tip too sharp and should be more flexible, but body design is appropriate) | Pass | Pass
USF_2_2 | swab w/ finely spaced rings | Marh 24th, 2020 | BIDMC | img/USF/USF_2_2.jpg |  |  | HP (Rick Fulop; ricfulop@desktopmetal.com) |  | Did not pass (tip too sharp and but apporpirately flexible, but body design is appropriate) | Pass
B_1 | swab w/very fine nubs | March 24th, 2020 | BIDMC | img/Baker/B_1 |  |  | Daniel Baker |  | Did not pass (tip is too sharp and ideally more flexible tip, but body design is appropriate) | Pass | Pass
S_1 | Swab w/ thick thread | March 24th, 2020 | BIDMC | img/Seriano/S_1 |  |  | David Seriano |  | Did not pass (tip is too sharp, but apporpiately flexible and body design is appopriate) | Pass | passed
S_2 | swab w/ fine spring | March 24th | BIDMC | img/Seriano/S_2 |  |  | David Seriano |  | Did not pass (tip is too sharp, but very flexible, perhaps too flexible, S1 may be better, and body design is appopriate) | Pass
S_3 | swab w/ fine thread | March 24th | BIDMC | img/Seriano/S_3 |  |  | David Seriano |  | Did not pass (tip is too sharp, and body design is appopriate) | Pass
S_4 | swab w/finely speaced rings | March 24th | BIDMC | img/Seriano/S_4 |  |  | David Seriano |  | Did not pass (tip is too sharp, and body design is appopriate) | Pass
S_5 | swab w/ low ring spacing | March 24th | BIDMC | img/Seriano/S_5 |  |  | David Seriano |  | Did not pass (tip is too sharp, and body design is appopriate) | Pass
S_6 | swab w/fine rings | March 24th | BIDMC | img/Seriano/S_6 |  |  | David Seriano |  |  | Pass
FT_1 | Foam Swab. Pt: HT1171B | March 24th, 2020 | BIDMC | Img/Foamtec/FT_1 |  |  | Foamtec International; Michael Strauss |  | Did not pass (diameter of tip too large, flexible bendable neck would be better) | Did not pass (not many cells collected)
FT_2 | Foam Swab. Pt: HT1501T2-5 | March 24th, 2020 | BIDMC | Img/Foamtec/FT_2 |  |  | Foamtec International; Michael Strauss |  | Did not pass (diameter of tip too large, flexible bendable neck would be better) | Did not pass (not many cells collected)
FT_3 | Foam. Pt. HT1501TC-5 | March 24th, 2020 | BIDMC | Img/Foamtec/FT_3 |  |  | Foamtec International; Michael Strauss |  | Did not pass (diameter of tip too large, flexible bendable neck would be better) | Did not pass (not many cells collected)
FT_4 | Foam Swab. Pt: HT1001-5 | March 24th, 2020 | BIDMC | Img/Foamtec/FT_4 |  |  | Foamtec International; Michael Strauss |  | Did not pass (diameter tip, diameter of tip too large, flexible bendable neck would be better) | Did not pass (not many cells collected)
EV_1 | DOWEL. For material testing | March 24th, 2020 | BIDMC |  | PCA 2000. 10 minutes. 100% |  | EnvisionTEC. Al Siblani. asiblani@envisiontec.com |  |  |  | passed
EV_2 | DOWEL. For material testing | March 24th, 2020 | BIDMC |  | PCA100 w/nitrogen | 2x10seconds w/nitrogen | EnvisionTEC. Al Siblani. asiblani@envisiontec.com
EV_3 | DOWEL. For material testing | March 24th, 2020 | BIDMC |  | PCA 100 w/nitrogen | 2x30seconds UV w/nitrogen | EnvisionTEC. Al Siblani. asiblani@envisiontec.com
EV_4 | DOWEL. For material testing | March 24th, 2020 | BIDMC |  | PCA 100 w/nitrogen | 2x20seconds w/nitrogen | EnvisionTEC. Al Siblani. asiblani@envisiontec.com
PVA | Chemical for material testing. Cas: 9002-89-5 | March 25th, 2020 | BIDMC |  | Polly(Vinyl Alcohol) |  | Sigma-Aldrich. Adama; Wyss |  |  |  | passed
Fil_Flt | White filament (for material testing) | March 25h, 2020 | BIDMC |  | 3DF-2 (Raw) (Polyurethane + PVA) |  | Adama; Wyss |  |  |  | passed
Fil_Lay | White filament (for material testing) | March 25th, 2020 | BIDMC |  | 3DF-1 (polyurethane + PVA) |  | Adama Sesay, Wyss Institude |  |  |  | passed
Sc_M | Jar filled with white substance | March 25th, 2020 | BIDMC |  | Scotch Magic Tape |  | 3M. dropped off by Adama Sesay; Wyss Institute
Sc_CC | Jar filled with white substance | March 25th, 2020 | BIDMC |  | Scotch Crystal Clear |  | 3M. dropped off by Adama Sesay; Wyss Institute
W_2_1 | White swab w/ silicon glue and sugar textured head | March 25th, 2020 | BIDMC | img/Wyss/W_2_1 | SG1. Silicon glue and sugar |  | Wyss Institute (Adama Shesay) |  | Did not pass (body design is appropriate, but tip/neck is too flexible and seems would not easily pass beyond external nares, seems non-uniform & wasn't sure if there would be scale-up reproducibility issues) | Pass
W_2_2 | Black swab w/ silicon glue and sugar textured head | March 25th, 2020 | BIDMC | img/Wyss/W_2_2 | SG2. Silicon glue and Sugar |  | Wyss Institute (Adama Shesay) |  | Pass (body design is appropriate, the tip end material seems very absorbent which we like, but the tip would ideally be more flexible, tip seems non-uniform & wasn't sure if there would be scale-up reproducibility issues) | Pass
W_2_3 | Rayon and crystal clear glue textured head | March 25th, 2020 | BIDMC | img/Wyss/W_2_3 | 3M1. Rayon fiber and scotch crystal clear glue head with polycarbonate swab |  | Wyss Institute (Adama Shesay) |  | Did not pass (tip sharp and inflexible but body design is appropriate, tip seems non-uniform & wasn't sure if there would be scale-up reproducibility issues) | Pass
W_2_4 | Rayon and magic tape textured head | March 25th, 2020 | BIDMC | img/Wyss/W_2_4 | 3M2. Rayon fiber with scoth magic tape swab head on a nylon swab |  | Wyss Institute (Adama Shesay) |  | Pass (tip is flexible and body design is appropriate) | Did not do cheek swab, uncured glue
W_2_5 | Rayon fiber and scotch crysal clear textured head | March 25th, 2020 | BIDMC | img/Wyss/W_2_5 | 3M3 Rayon Fiber with scotch crystal clear textured head on nylon swab |  | Wyss Institute (Adama Shesay) |  | Pass (tip is flexible and body design is appropriate, tip seems non-uniform & wasn't sure if there would be scale-up reproducibility issues) | Pass
W_2_6 | Rayon fiber/ Scotch magnetic tape textured head | March 25th, 2020 | BIDMC | img/Wyss/W_2_6 | 3M4 Rayon Fiber/Scotch magic tape textured head on polycarbonate head |  | Wyss Institute (Adama Shesay) |  | Did not pass (tip is sharp and inflexible but body design is appropriate, tip seems non-uniform & wasn't sure if there would be scale-up reproducibility issues) | Did not do cheek swab, uncured glue
W_2_7 | Nylon fiber/magic tape | March 25th, 2020 | BIDMC | img/Wyss/W_2_7 | 3M5 Nylon Fiber/Magic Tape textured head on polycarbornate swab |  | Wyss Institute (Adama Shesay) |  | Pass (tip would ideally be more flexible but body design is appropriate, tip seems non-uniform & wasn't sure if there would be scale-up reproducibility issues) | Pass
W_2_8 | Nylon fiber/magic tape | March 25th, 2020 | BIDMC | img/Wyss/W_2_8 | 3M6 Nylon Fiber/magi tape textured head on nylon swab |  | Wyss Institute (Adama Shesay) |  | Pass (tip ideally would be more flexible, but design is appopriate, tip seems non-uniform & wasn't sure if there would be scale-up reproducibility issues) | Pass
W_2_9 | Nylon FIber/Crystal Clear | March 25th, 2020 | BIDMC | img/Wyss/W_2_9 | 3M_7 Nylong fiber/ crystal clear textured head on a nylon swab |  | Wyss Institute (Adama Shesay) |  | Pass (tip is flexible and body design is appropriate, tip seems non-uniform & wasn't sure if there would be scale-up reproducibility issues) | Pass
W_2_10 | Nylon fiber/magic tape | Martch 25th, 2020 | BIDMC | img/Wyss/W_2_10 | 3M8 nylon fiber/magic tape texted head on a nylon swab |  | Wyss Institute (Adama Shesay) |  | Pass (tip is more flexible which we like but body design is appropriate, tip seems non-uniform & wasn't sure if there would be scale-up reproducibility issues) | Pass
W_2_11 | Nylon FIber/ crytal clear textured head | March 25th, 2020 | BIDMC | img/Wyss/W_2_11 | 3M9 nylon fiber w/ crystal clear textured head on polycarb |  | Wyss Institute (Adama Shesay) |  | Did not pass (too sharp and tip too inflexible) | Pass
W_2_12 | Sugar on nylon | March 25th, 2020 | BIDMC | img/Wyss/W_2_12 | PDMS [sugar on nylon] |  | Wyss Institute (Adama Shesay) |  | Did not pass (tip/neck are too flexible we feel like it would get caught in the external nares and not pass deeper well) | Pass | Pass
EV_2_1 | 3cm rods (for material testing) |  |  |  | C 29C |  | EnvisionTEC. Al Siblani. asiblani@envisiontec.com
C_3 | 4mm voro | March 26th, 2020 | BIDMC | img/Carbon/C_3 | keysplint Soft Clear | dreve PCU 90 N2 15 min | Carbon3D. Keshav Swarup |  | Did not pass (tip head too firm, would create a neck for more flexibility at the end, and would put breakpoint from tip head end at least 7-10cm from the end. |  | *pass (presumably same material as C!)
C_4 | 3mm voro | March 26th, 2020 | BIDMC | img/Carbon/C_4 | keysplint Soft Clear | dreve PCU 90 N2 15 min | Carbon3D. Keshav Swarup |  | Did not pass (tip head too firm, would create a neck for more flexibility at the end, and would put breakpoint from tip head end at least 7-10cm from the end). |  | *pass (presumably same material as C!)
C_5 | USF | March 26th, 2020 | BIDMC | img/Carbon/C_5 | keysplint Soft Clear | dreve PCU 90 N2 15 min | Carbon3D. Keshav Swarup |  | Did not pass (tip head too sharp and stiff although bristeled head may perform better ultmately for specimen capture. Body design is good) |  | *pass (presumably same material as C!)
C_6 | long bulb | March 26th, 2020 | BIDMC | img/Carbon/C_6 | keysplint Soft Clear | dreve PCU 90 N2 15 min | Carbon3D. Keshav Swarup |  | Pass (unique design, and may be preferable to others given logner head/more absorption, and flexibility of entire head while maintaining shape well after deformation) |  | *pass (presumably same material as C!) | **likely a good design, the head is longer and flexible and probably can pass deeper as well as pickup more material
C_7 | 3mm 1.5mm neck | March 26th, 2020 | BIDMC | img/Carbon/C_7 | keysplint Soft Clear | dreve PCU 90 N2 15 min | Carbon3D. Keshav Swarup |  | Pass (body design std Copan, tip soft enough) |  | *pass (presumably same material as C!)

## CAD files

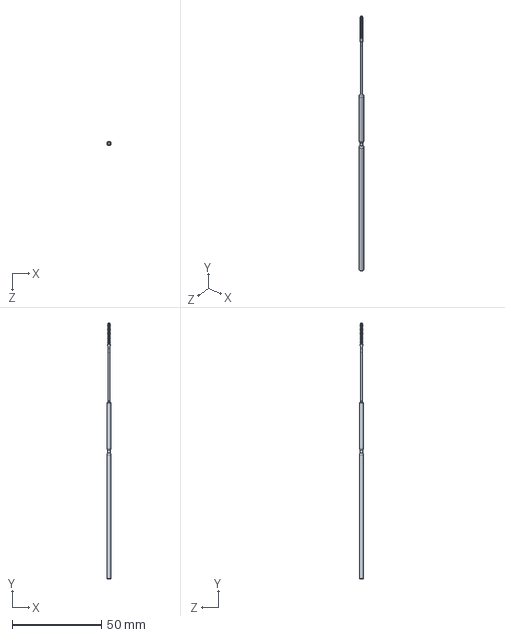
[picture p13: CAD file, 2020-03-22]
design_files/FATHOM_Swab/FATHOM_xMasSwab_1.0mmCoreExtended.SLDPRT
2.50 x 143.5 x 2.50 mm

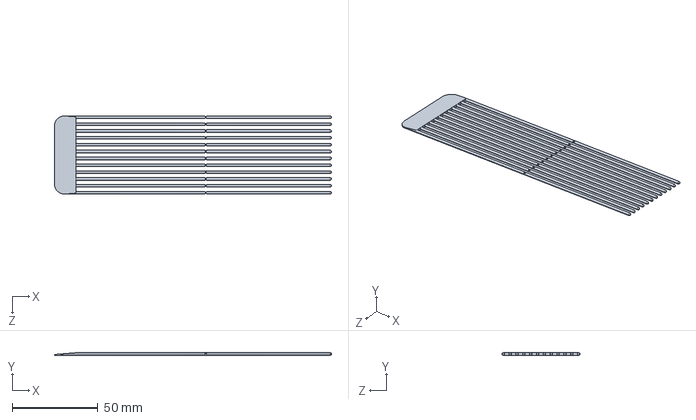
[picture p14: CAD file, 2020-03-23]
design_files/Harvard/3D Printed Entire Swab/swab_Round v1.2a.STEP
161.8 x 1.57 x 45.6 mm

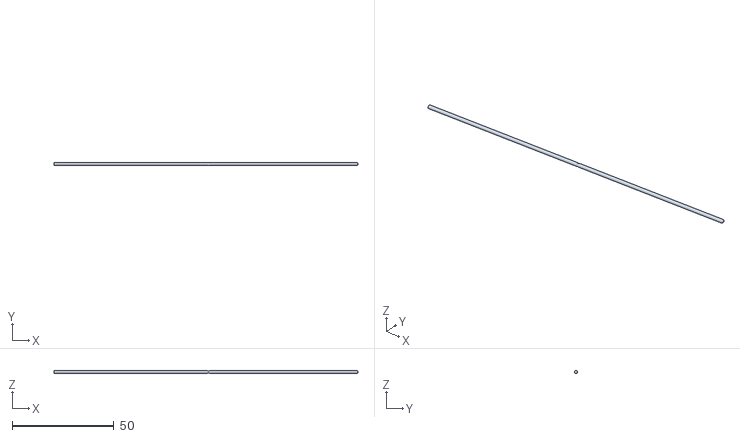
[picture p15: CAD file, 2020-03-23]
design_files/Harvard/3D Printed Shaft+Adhesive+Swab/swab_Round v1.2a-shaft only.STL
149.1 x 1.57 x 1.57

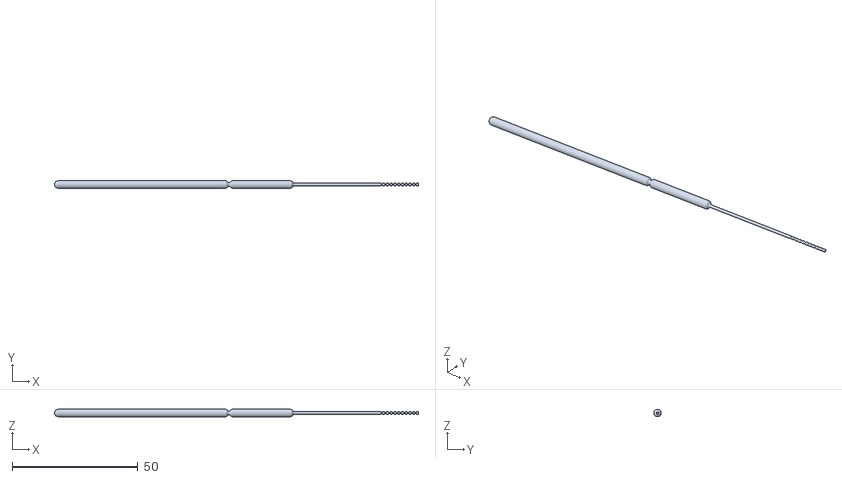
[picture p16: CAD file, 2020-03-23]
design_files/Swab test 4 (Wyss).STL
145.0 x 3.00 x 3.00

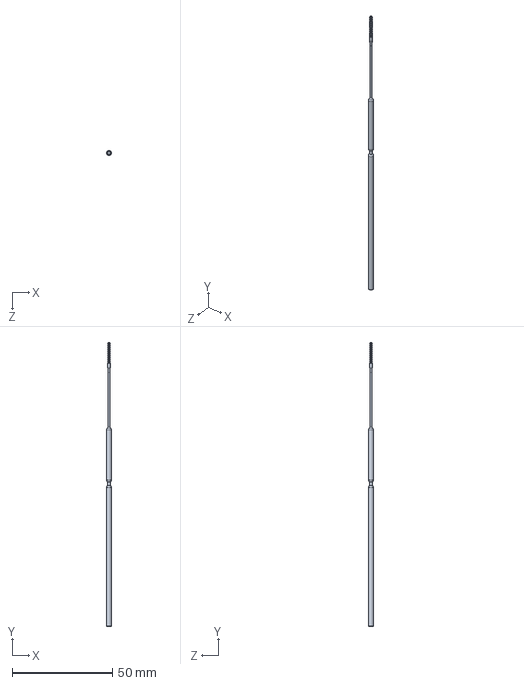
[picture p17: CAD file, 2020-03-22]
design_files/FATHOM_Swab/FATHOM_xMasSwab_1.0mmCore.SLDPRT
2.50 x 142.0 x 2.50 mm

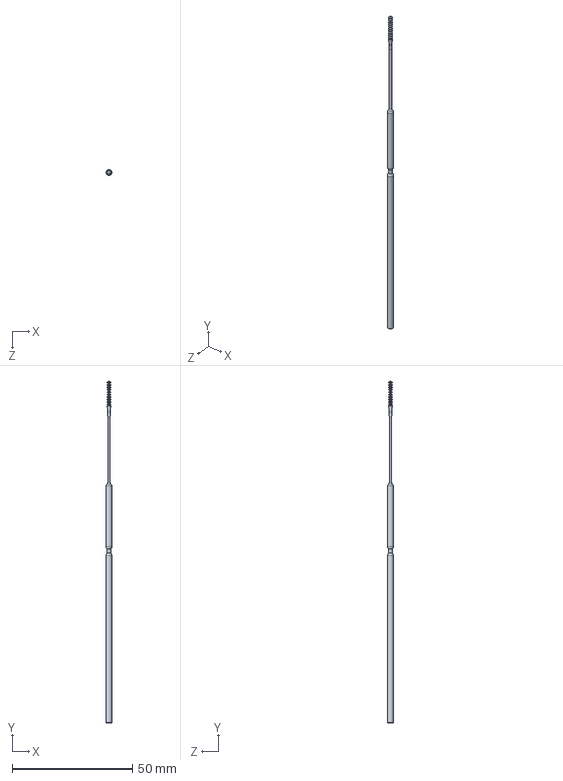
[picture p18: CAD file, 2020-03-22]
design_files/FATHOM_Swab/FATHOM_xMasSwab_0.5mmCore.SLDPRT
2.50 x 142.0 x 2.50 mm

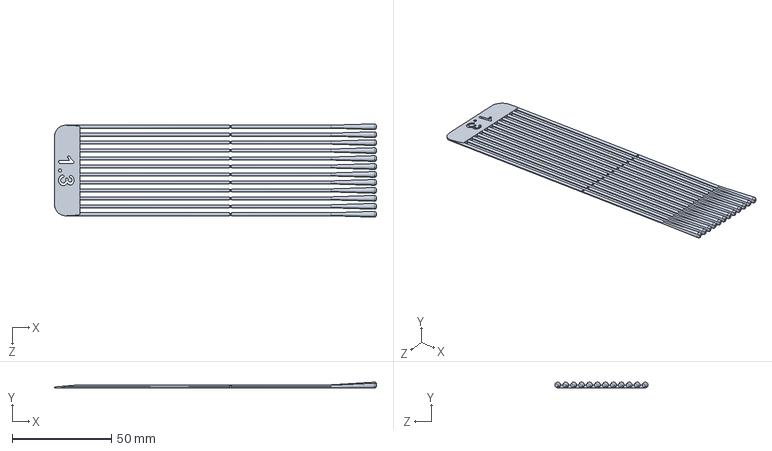
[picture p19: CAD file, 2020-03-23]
design_files/Harvard/3D Printed Shaft+Adhesive+Swab/swab_Round v1.3.STEP
161.8 x 2.93 x 46.9 mm

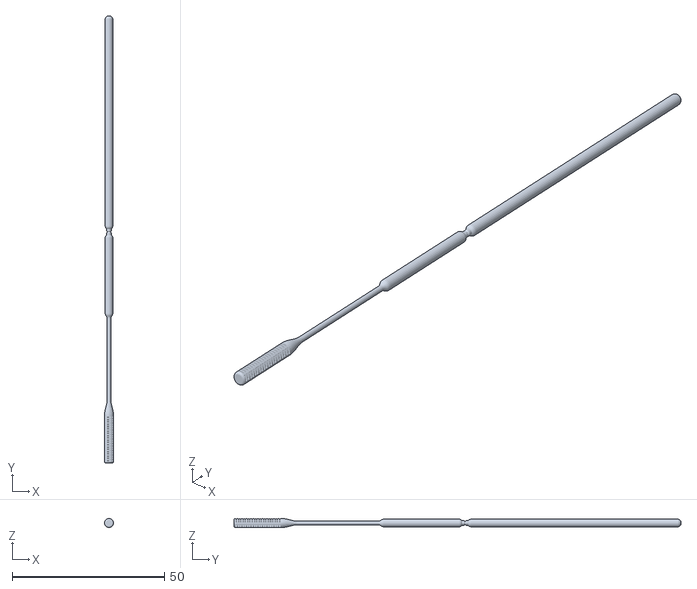
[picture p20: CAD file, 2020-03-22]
design_files/FATHOM_Swab/200322_RidgeSwabs_BreakoffChamferAdded_ShaftDiameter1.25mm/200322_FATHOM_SmallSquareHoles_Swab.stl
3.00 x 147.0 x 3.00

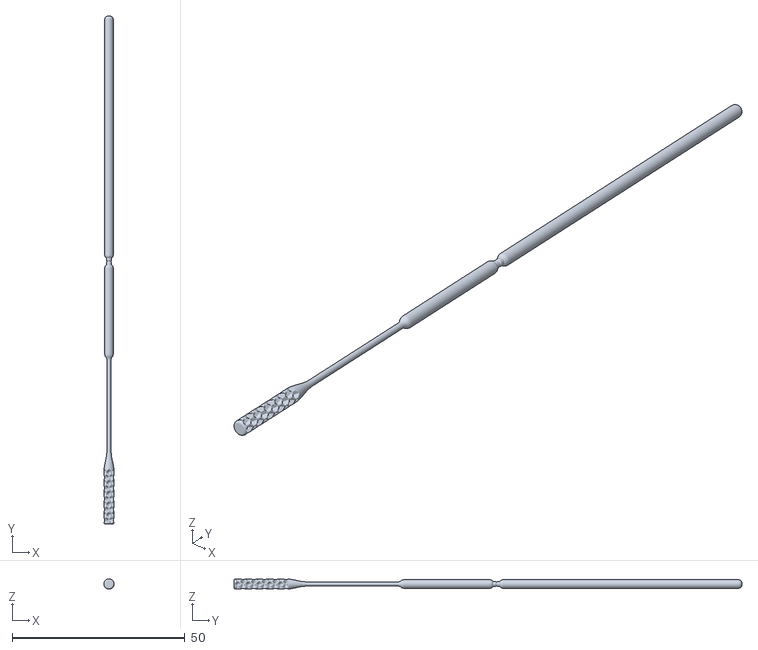
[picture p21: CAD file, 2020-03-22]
design_files/FATHOM_Swab/200322_RidgeSwabs_BreakoffChamferAdded_ShaftDiameter1.25mm/200322_FATHOM_Hexagon_Swab.stl
3.00 x 147.0 x 3.00

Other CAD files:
design_files/Harvard/3D Printed Shaft+Adhesive+Swab/swab_Round v1.2.STEP
design_files/Harvard/3D Printed Shaft+Adhesive+Swab/swab_Round v1.1.STEP
design_files/FATHOM_Swab/200322_RidgeSwabs_BreakoffChamferAdded_ShaftDiameter1.25mm/200322_FATHOM_SquareHoles_Swab.stl
design_files/FATHOM_Swab/200322_RidgeSwabs_BreakoffChamferAdded_ShaftDiameter1.25mm/200322_FATHOM_Hexagon_Swab.f3d
design_files/FATHOM_Swab/200322_RidgeSwabs_BreakoffChamferAdded_ShaftDiameter1.25mm/200322_FATHOM_SmallSquareHoles_Swab.f3d
design_files/FATHOM_Swab/200322_RidgeSwabs_BreakoffChamferAdded_ShaftDiameter1.25mm/200322_FATHOM_SquareHoles_Swab.f3d
design_files/FATHOM_Swab/FATHOM_xMasSwab_0.5mmCore.STL
design_files/FATHOM_Swab/FATHOM_xMasSwab_1.0mmCore.STL
design_files/FATHOM_Swab/FATHOM_xMasSwab_1.0mmCoreExtended.STL

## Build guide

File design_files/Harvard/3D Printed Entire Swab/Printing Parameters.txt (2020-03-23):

-- Shaft only .stl file attached

Printers:

Fortus 450mc, ULTEM 1010, Solid Infil, .010" layers, T14 Tip

Fortus 450mc, PC-ISO, Solid Infil, .010" layers, T16 Tip

Fortus 450mc, Nylon12CF, Solid Infil, .010" layers, T20 Tip

Markforged Mark Two: Onyx, 100% rectangular infil, .1mm layers, 2 perimeter walls

-- Shaft with USF Swab

Fortus 450mc, ULTEM 1010, Solid Infil, .010" layers, T14 Tip

Markforged Mark Two: Onyx, 100% rectangular infil, .1mm layers, 2 perimeter walls

Objet Connex 3 500, Digital ABS (RGD531/RGD515), 30 micron layers, matte surface

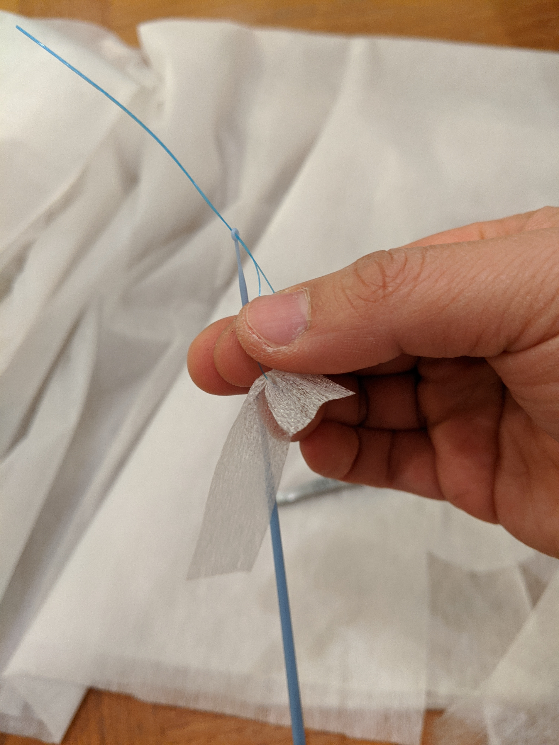
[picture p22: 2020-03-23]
img/Jenny/DIYswab/threading setup.jpg

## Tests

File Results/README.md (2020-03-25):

*Last modified: Wednesday, March 25, 2020*

# Results summary, BIDMC

This document summarizes BIDMC's evaluation of dozens of [**geometries**](#geometries) (swab designs) and [**materials**](#materials) ([full data here](np_swab_results.xlsx)), with brief comments on [**decontamination/sterilization** and **packaging**](#decon), [**production volume**](#volume), and [**clinical trials**](#trials).

- <a href = "#geometries">Geometries</a>
- <a href = "#materials">Materials</a>
- <a href = "#decon">Decontamination/sterilization and packaging</a>
- <a href = "#volume">Production volume</a>
- <a href = "#trials">Clinical trials</a>
- <a href = "#contact">Contact</a>

## Geometries

**Note:** examples shown are not necessarily the preferred material and not necessarily from the manufacturer who created the design. No attribution of credit is made or implied by this listing.

### Tip

Tip should:

- collect sufficient material (see Gram stains below)
- not end in a sharp tip (e.g., spring geometry ends in sharp tip; if tip is connected to support regardless of geometry, result is a sharp tip)
- maximize surface area
- be flexible (more flexible than bic pen)
- restore elastically to straight (even after multiple bending)

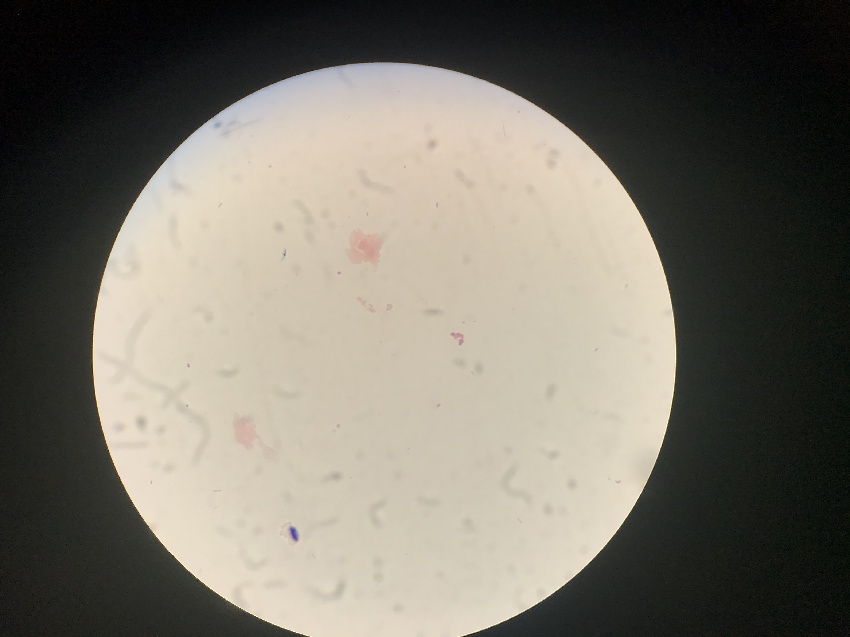
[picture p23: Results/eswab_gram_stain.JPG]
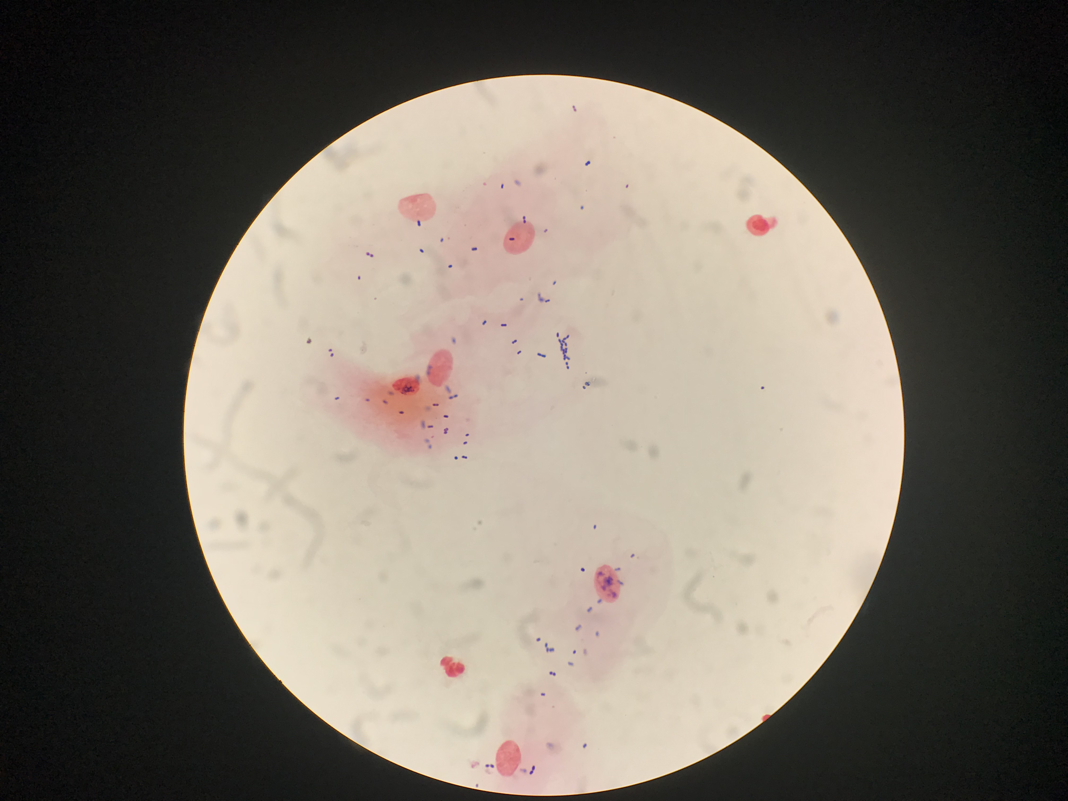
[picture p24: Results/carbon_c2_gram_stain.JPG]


Reference (left) and passing-quality (right) Gram stains of cheek swabs. Epithelial cells (large faint pink) and (Gram-positive) bacteria (small purple) are clearly seen. Many Gram stains of the prototype NP swabs under evaluation (like the one at right) collected more material than the reference (left), but this should not be interpreted quantitatively (a lot/a little), only qualitatively (yes/no).

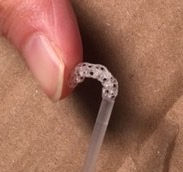
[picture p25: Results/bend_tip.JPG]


Tip flexibility

#### Preferred tip:

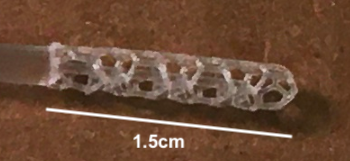
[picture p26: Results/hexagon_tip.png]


Hexagon (Carbon3D)

This was preferred because the hollowness captured a lot of material, while also being reasonably stiff. This was not a strong preference.

#### Also acceptable (no order):

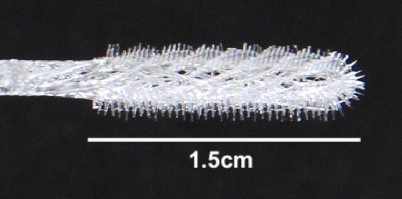
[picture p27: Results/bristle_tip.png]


Bristle (OPT)

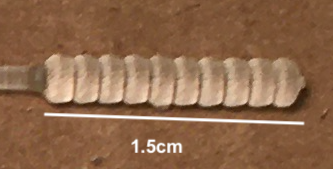
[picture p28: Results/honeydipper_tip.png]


Honeydipper (FormLabs) 

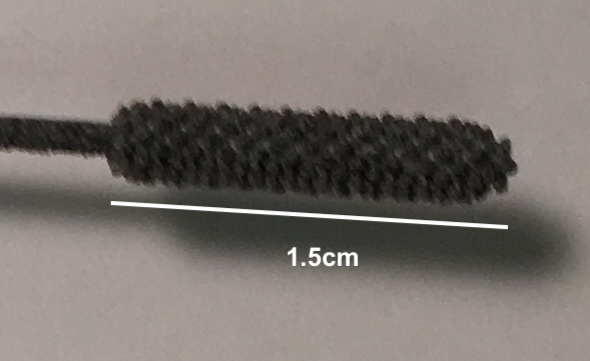
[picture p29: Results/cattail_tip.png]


Cattail (HP print of ?USF design)

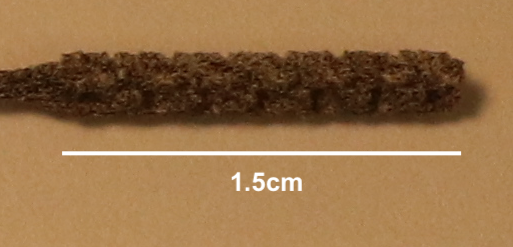
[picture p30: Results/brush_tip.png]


Brush (HP print of ?USF design)

Note none of these are [flocked]("https://github.com/HMS-RIC/Covid19-NP-Swab/#flock"). FDA says flock is **preferred** but **not required**.

### Shaft

#### Preferred shaft:

3mm-diameter tip, 1mm-diameter neck, 2.5mm-dimater handle and \~2mm breakpoint located 7cm from tip-end of swab.

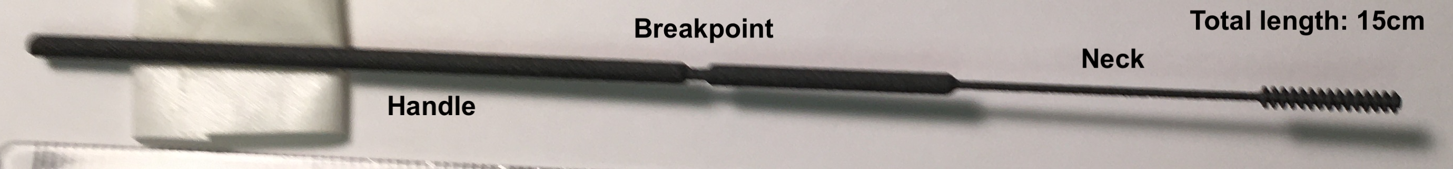
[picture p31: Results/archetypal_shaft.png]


Archetypal (Abiogenix design (?), HP print)

### STL files

We do not have all stl files for all designs tested; what we have are [here](../design_files/). If you need one we don't have, please contact its [creator](np_swab_results.xlsx)). If you have an stl file to share, please email it to ccallah@bidmc.harvard.edu with *STL-FILE_\<identifier>_\<company>* in the subject field.

## Materials

### Handling

Key features (best performers in parentheses): 

- straight (HP > Carbon3D, FormLabs)
- smooth to the touch (Carbon3D > FormLabs, HP)
- dry (not sticky) (Carbon3D, HP, FormLabs)
- shaft: stiffness comparable to that of the inkholder of a bic pen
- neck and tip: flexible (capable of being bent 180 degrees without breaking, except at the breakopint) (HP, Carbon3D)
- breaks at breakpoint (should be somewhat difficult to do) (HP, FormLabs)
- no dust or other byproduct of printing process

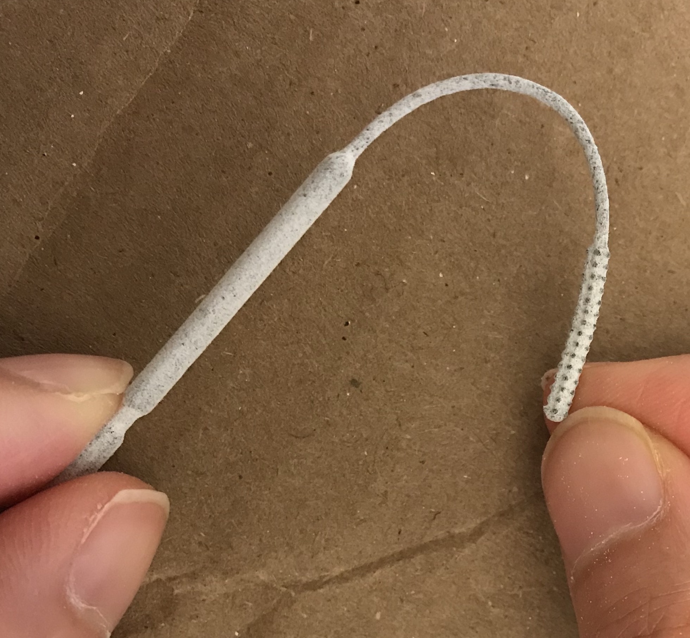
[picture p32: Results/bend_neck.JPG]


Neck flexibility

#### Preferred material:



Keysplint Soft (Carbon3D)

### PCR compatibility

All materials tested so far (as of March 25, 2020) are PCR compatibile (see Excel for any codenames).

**Passed:** OPT, HP ("USF-1"), EnvisionTec (Nilson), FormLabs, Carbon3D, Pavel.

**Pending:** J_1 (Jifei), USF-2, B_1, S_1 (Seriano), EV.

**Not tested (failed clinical testing):** FT

**Not listed here:** materials from compound manufacturing (shaft plus glue plut flock/PDMS)

## Decontamination/sterilization and packaging

Autoclaving preferable, isopropanol or 70% ethanol washes with clean packaging acceptable.

Likely process: swabs produced and washed at scale, then:

- (option 1) take to a company with autoclavable paper packaging (e.g. Georgia-Pacific, 3M), or

- (option 2) packaged at manufacturer's site (e.g. EnvisionTec)



EnvisionTec's packaging

## Production volume

To my knowledge EnvisionTec, HP, FormLabs, and Carbon3D all have capacity for producing at least hundreds of thousands per day.

## Field testing, safety, market

**Field testing.** Field testing means using swabs on nasopharynx of people with confirmed SARS-CoV-2.

At BIDMC we have tested for appropriateness by (infectious disease/clinical pathologist) expert evaluation, and tested for sufficiency of collection using cheek swab and Gram stain as a surrogate for viral particle collection from nasopharynx. We have **not** field tested.

Field testing requires IRB approval.

To my knowledge Dr. Summer Decker at USF has field-tested at least on non COVID-19-suspected cases. She has an IRB.

I suggest as a first step other clinical sites model after USF's IRB and have their local IRBs cede review to USF as URB of record.

**Safety.** Note swabs are FDA Class-1 exempt devices; "garage testing" not advised.

**Market.** Several tip/shaft/material combinations will likely yield usable products. There will be a competitive market. A/B testing, marketing, contracting, etc. are beyond the scope of this document.

## Contact

Ramy Arnaout, MD, DPhil rarnaout@bidmc.harvard.edu 617-538-5681 on behalf of the BIDMC team (not everyone is pictured):



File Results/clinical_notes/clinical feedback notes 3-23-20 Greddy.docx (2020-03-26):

Clinical Feedback meeting notes by Goutam Reddy (greddy@abiogenix.com)

3/23/20 meeting @ Stanford Health

Interviewed: Dr. Linda Barman, Thanh Khong PAC (they run the drive-through swabbings)

Summary of Design Notes:

1) Features too sharp => need a smoother edge (like flocking) - suggested a “rounded Archimedes screw”
2) Need a rounder tip (like bulb of flocked head) w/ “cupping”
3) Need to stiffen break-point and move back
4) Need plastic to bend but not deform => spring back after bending (liked thicker diameter neck models than thinner)
5) Most liked designs #3, #10, #1
6) Finer features not showing up in PA12 prints (PA11 vs PA12?)

Swab Note:

They use a swab with a longer cut-off point. She said our cut-off point was too short (nasal swab vs. nasopharyngeal swab?) Measurements of the swabs they use below:


General Notes:

1) We should test temperature changes of our swabs as they can be sitting in freezing temperatures for drive-through clinics.
2) Asked about sterilization and packaging -> is it autoclavable?
3) Nasopharngeal space is extremely sensitive (to bleeding, irritation etc…), especially in patients coming in to be swabbed. Err on the side of doing no harm (i.e. swabbing is not a life-saving intervention => we’ll be doing millions of swabs => err on side of gentle np swab and no damage to tissues (no poking, soft interface, no breaking off inside so ENT has to extract)

Test 1) Abiogenix Nubs w/ Holes in PA11 (mfg by HP in San Diego)


- too flimsy @ breakoff point => stiffen @ breakoff
- breakpoint too far down
- too rough

Test 2) Abiogenix Nubs w/o Holes in PA11 (mfg by HP in San Diego)


- needs rounded tip like the bulb on the flocked swab
- tip is too tiny: needs absorption
- passage to nasopharynx has bends, so swab needs to bend but needs to spring back

Test 3) Fathom ??? in PA12 (mfg by Fathom in Oakland)


- liked round tip
- smooth out
- make neck longer
- good size
- good front
- good neck

Test 4) Fathom ??? in PA12 (mfg by Fathom in Oakland)


- too brittle
- ripped off tip
- too small
- too thin
- not sure which one this was – check inventory of prints from 3/23/20

Test 5) Fathom ??? in PA12 (mfg by Fathom in Oakland)


- heads breaking off
- “medieval torture device”
- shaft too brittle

Test 6) Abiogenix Nubs in PA12 (mfg by Fathom in Oakland)


- “weapon”
- shaft breaking
- in general: needs rebound: needs higher elasticity

Test 7 & 8) Abiogenix Round Tip in PA12 (mfg by Fathom in Oakland)


- no notes

Test 9) Fathom ??? in PA12 (mfg by Fathom in Oakland)


- Tip ripped off
- Too small
- Too thin

Test 10) Wyss Balls in PA12 (mfg by Fathom in Oakland)


- “head too wide”
- like roundness
- suggested archimedes screw => rounded w/ cupping and capture fluid, like a “staircase with smooth edges”

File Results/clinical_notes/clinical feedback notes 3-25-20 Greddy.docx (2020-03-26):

Clinical Feedback meeting notes by Goutam Reddy (greddy@abiogenix.com)

3/25/20 meeting @ Stanford Health

Interviewed: Dr. Linda Barman, Thanh Khong PAC (they run the drive-through swabbings)

Summary of Design Notes:

1) Most liked designs #15 > #13 > #11
2) Liked rounded tips
3) Liked wider necks
4) Liked USF design because it had a 100mm break-point with longer neck
5) Materials Comparison:

They liked PA11 the best because of the springback of the neck.

PA12G (gray) was too stiff and PA12W (white) was too weak.

Requested feel of a slightly stiffer PA11.

6) Want more elasticity from designs (spring-back). The nasopharynx has a kink ( "a little hill" and go down; want overall trajectory to be straight but go over the hill)

Swab Note:

The swab Stanford Health is using is Copan 503CS01, which has a 100mm breakpoint.

They both said our cut-off point was too short (again). See previous note for full measurements.

General Notes:

1) We should autoclave our swabs first to test material change prior to testing, and test at different temperatures.
2) For sterility, they suggested EtO as more commonly available than autoclave (globally).
3) Dr. Barman suggested a pre-bend/kink in neck of 5-10 degrees to assist with downward push.
4) Dr. Barman suggested making a spiral structure in neck to strengthen it
5) There are two techniques for swabbing:
  a. one is “twirling” - rotating the swab in the fingertips 5 times after insertion for 10 seconds
  b. the other is “swirling” (moving the hand with a circular motion)

Suggest we include training materials if there is a preferred way to use this swab.

6) drive-through patients: prefer to have patients look ahead or slightly turned so they can use the headrest for patient to push back against when expecting recoil of head from insertion of np swab

Test 11) Wyss Spiral in PA12 (mfg by Fathom in Oakland)


- like it; not bad; - as long as it doesn't break - too flexible: may jam in their nose - too brittle - you’re gonna get jammed up; make it less brittle and stiffer - breaks too easily | | | are you gonna get locked up; make it less brittle and stiffer | | | breaks too easily

Test 12) USF PA11 (mfg by HP in San Diego)


- liked burr tip
- note burrs do not come out in prints
- neck flexed and broke
- like that the breakpoint is moved up
- feels more like it won’t break in my hand
- feels harsh, too brittle, but like length
- check at different temperatures
- NOTE: burrs are inconsistent (too small features) for current MJF tech;
- worry burrs may fall/rub off in nasopharynx

Test 13) Fathom Squares Large (mfg by Fathom in Oakland)


- really like rounded tips
- doesn’t feel bad; spring is good
- make neck longer (worried neck is thick too soon; that part goes in nares (neck) ; worried it won't go as deep; narrower and longer neck; like crevices
- check on structural integrity

Test 14) Fathom Squares Tiny (mfg by Fathom in Oakland)


- check with fluid collection
- like roundness and roughness (not too rough)
- NOTE: features did not come out that well in this model

Test 15) Fathom-Branan Screw (mfg by Fathom in Oakland)


- do a torsional test
- great that it’s a little wider [than below designs]
- “my favorite”, “top choice”
- nice rounded top

Test 16, 17, 18, 19) HP Screw and Spring Designs Wide (mfg by HP Vancouver)


- too flexible
- won't be able to go through
- too pointy at end ; too pokey
- neck too brittle/ fragile => make thicker
- may not be wide enough
- too wimpy ; really breakables;
- not hard enough to guide
- head too small
- really didn’t like PA12W materials

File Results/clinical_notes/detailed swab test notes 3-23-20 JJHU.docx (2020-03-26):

Today’s testing focused on the Abiogenix swab design with a nubbed tip (https://github.com/HMS-RIC/Covid19-NP-Swab/tree/master/design_files/abiogenix_swab_nubs), modified and printed in PA11 by HP, and also standardizing test methods (updated in https://github.com/HMS-RIC/Covid19-NP-Swab/blob/master/Testing/Testing%20Procedures.md).

For comparison I also used the same design printed in a proprietary epoxy on an SLA printer (this is not one of the official materials under consideration), and a Copan NP swab. Swabs were done by a doctor who has been doing shifts at a drive-through test site and grabbed a couple extra swabs on her way over.

Test 1, clinical evaluation:

- The SLA part is the stiffest, followed by Copan, then PA11. All were flexible but strong enough to maneuver through narrow passages (push through a lightly closed fist) and none felt too fragile. The tip was rough when jabbed into the back of the hand but not painful.
- The flocking was nice and soft on fingertips and was nicer in the lower nostril but I couldn’t tell a difference higher up.
- Doing the NP swabs on the doctor (person A) and me, both of us had one fairly blocked nostril and one clear one. There didn’t seem to be much of a difference in being able to get to the NP between the different swabs. For me all three caused a burning/stinging sensation once they were past the nasal cavity but none felt worse than the others. The general sensation and overall experience was unpleasant enough that I didn’t notice any difference between the Copan flocked tip and the others. Person A didn’t get a Copan swab but said both printed parts were acceptable to use and to have the test done.
- Snapping off – she’s been actually putting the VTM vial in a holder in front of her and grabbing the swabs with both hands on either side of the break point to snap it in two. That was easy for both printed parts. I snapped them off against a 15ml falcon tube, worked perfectly on the first try for both parts.

Test 2, sample collection

- All swabs came out wetted, most with some visible mucus between the rows of nubs. Rotating against the NP seems to have ‘spooled’ strands of mucus around the swab, captured between nubs (couldn’t get an in-focus picture of this). Swiping the 3D printed designs against a slide didn’t visibly leave much behind, sometimes just an array of dots as the nubs contacted while rolling the swab tip against the slide. The 3D printed swab smears only covered ~5-20% of the slide area covered by a smear from a cotton swab or the Copan swab (almost continuous coverage)
- To try and pull more material off the swab for staining we tried putting a drop of buffer (used EPA water but saline or PBS would work) then rolling the swab back and forth through the liquid.
- Results!
  - Don’t have a great way to count cells and field of view isn’t big enough to get a great idea of density so at the end are links to videos of panning over the various slides, all at the same magnification. Note I’m currently getting over a sinus infection and my samples are completely full of grossness even though I wasn’t that mucus-y. Conclusions below if you don’t have time to watch the videos.
  - More material was visibly transferred to the slide from the direct (no extra buffer) smear, probably because the mucus stuck directly to the dry slide but not as well to a wet slide. Staining showed plenty of bacteria in the mucus steaks for both methods, but loose cells/bacteria were much more common in the samples smeared with buffer.


- My conclusions:
  - if the swab comes out coated with a visible amount of wet sample either filling/inside the swab or sitting on the swab (not fully absorbed inside), it has cells/bacteria inside that fluid and has probably picked up enough sample to be useable for PCR. See https://www.dropbox.com/s/wlb316jv5kuow6q/IMG_20200323_193553%5B1%5D.jpg?dl=0 , if you zoom in you can see mucus between the nubs and fluid filling in the rest of the volume of the tip.
  - If the swab has enough fluid/mucus sticking out from the tip to leave a smear on the slide, that will give a representative idea of what cells/bacteria are being picked up. If the swab looks “dry” or after attempting to smear no material is visibly left on the slide then I would recommend rolling it in a drop (50ul worked well for the methylene blue assay, gram stain may be different) of fluid on the slide to help wash material off of the swab to make sure material isn’t just ‘trapped’ inside the swab geometry in a way that could elute but won’t smear well. Video of this method here: https://www.dropbox.com/s/coizu1qvzxpvwau/cheek%20swab%26stain%20w%20methylene%20blue%20for%20spiky%20swabs%20using%2050ul%20buffer%20to%20wet%20swab.mp4?dl=0
  - The 3D printed swabs are definitely yielding less than the Coban swab, but with the quick staining method we really can’t tell how much of that is due to sample collection vs sample transfer to the slide. I’ll follow up with Dr. Ray Monnet at UW who suggested doing a study of sample collection efficiency (using a controlled viral stock solution) from our various swabs vs commercial but don’t think that should block us from moving forward for now – it would just be a useful data point on the expected relative sensitivity of the 3d printed vs manufactured swabs when viral counts are low.
  - Updated the testing page (https://github.com/HMS-RIC/Covid19-NP-Swab/blob/master/Testing/Testing%20Procedures.md) with a method to compare the absorbancy of different swabs with fairly available tools, but the swab+stain test sems the most relevant, so maybe it’s worth just finding nearby microbiology labs who can help with that work. I mixed up the methylene blue in ~15 minutes and each sample takes 5-10 minutes to swab, stain, image.

Test 3: PCR

- Gave samples of the HP PA11 material to UW virology for testing. A friend will autoclave more PA11 samples tomorrow and if both those tests pass we’ll also PCR the autoclaved samples to make sure the high temps don’t damage the plastic in a way that affects the reaction. Should also have PA12 samples in hand for PCR test tomorrow.

My overall conclusions from tests 1-2. I think we can make a completely (non-flocked) 3D printed part that is clinician/patient acceptable and while less effective than the Coban swab, in most cases collects enough sample for a positive ID. From my sample size of 2 (my friend and the medical assistant who swabbed me for my real test last week) the people who are going to be doing high throughput swabbing don’t have a ton of training on this and aren’t going to be too picky, and from their point of view patients are super grateful to be getting the test and can tolerate the brief discomfort/even slight pain. So we should put effort towards not making this a torture device but don’t need to optimize too much here for the first short term “fill the immediate gap” run.

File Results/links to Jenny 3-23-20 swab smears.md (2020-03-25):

stained swab smears to go along with [results from 3/23/20 testing](https://github.com/HMS-RIC/Covid19-NP-Swab/blob/master/Results/detailed%20swab%20test%20notes%203-23-20%20JJHU.docx)  . Above the line are all NP swabs, below are cheek swabs for comparison.

Links are to video files since I didn't have another good way to show the density of cells on the slides. Tried to get representive screenshots that weren't just full of mucus.

[Jenny PA11 abiogenix nubs design smeared with 50ul buffer](https://www.dropbox.com/s/vpmz2sq5rdnwm7u/Jenny%20left%20nostril%20PA11%20nubs%20smeared%20w50ul%20EPA%203Xview.mp4?dl=0)
(there is actually stuff in there if you watch the video, it's just not in huge clumps)



[Jenny Copan smear](https://www.dropbox.com/s/cd7lqqm1viiilww/Jenny%20RightNostril%20Copan%20smear%203Xview.mp4?dl=0)



[Jenny SLA abiogenix nubs design smear](https://www.dropbox.com/s/poj2g0lwtozlrp3/Jenny%20RightNostril%20SLA%20nubs%20smear%20only%203Xview.mp4?dl=0)



[Jenny SLA abiogenix nubs design smeared with 50ul buffer](https://www.dropbox.com/s/vbcg39j998iqoxt/Jenny%20rightNostril%20SLA%20nubs%20smeared%20w50ul%20EPA%203Xview.mp4?dl=0)



[person A PA11 abiogenix nubs design smeared with 50ul buffer](https://www.dropbox.com/s/f5tjcwmfs07rnh1/person%20A%20left%20nostril%20PA11%20nubs%20swab%20smeared%20w50ul%20EPA%203Xview.mp4?dl=0)

[person A SLA abiogenix nubs design smeared with 50 ul buffer](https://www.dropbox.com/s/2jhyipl4g09thzc/person%20A%20left%20nostril%20SLA%20nubs%20swab%20smeared%20w50ul%20EPA%203Xview.mp4?dl=0)

[person A SLA abiogenix nubs design smear](https://www.dropbox.com/s/w5t8wzo1z7ok02v/personA%20left%20nostril%20SLA%20nubs%20swab%20smeared%203Xview.mp4?dl=0)

---
Did some cheek swabs for comparison

[Jenny cheek swab with PA11 nubs design smeared directly](https://www.dropbox.com/s/a4lbwno24mw98x0/J_HP_PA11_nubs_smearonly_3x_cheek.mp4?dl=0)



[Jenny cheek swab with PA11 nubs design smeared w/50ul buffer](https://www.dropbox.com/s/xeh0nvsf753mn3h/J_HP_PA11_nubs_smear50ul_3x_cheek.mp4?dl=0)



[Jenny cheek swab PA12 honeypot design smeared w/50ul buffer](https://www.dropbox.com/s/dtv5omgsninmkof/J_HP_PA12_honeypot_3x_cheek.mp4?dl=0)



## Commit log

2020-03-22 Add files via upload
    OPT Industries' swab design and printed result
2020-03-23 Daily results update
    [np_swab_results.xlsx]
2020-03-23 Specimen ID
    [np_swab_results.xlsx]
2020-03-23 Formlabs material update
    [np_swab_results.xlsx]
2020-03-24 Add files via upload
    notes on user feedback and sample collection testing on the HP PA11 "nubs" design, thoughts on test methods.
2020-03-24 Images added. Results updated
    [np_swab_results.xlsx, np_swab_results_03_23_2020.xlsx, np_swab_results_03_24_2020.xlsx]
2020-03-24 fixed result name
    [np_swab_results.xlsx]
2020-03-24 added designs and videos from Carbon
    [3mm_2.75cs_0.45d_1.5neck.stl, long bulb test.stl]
2020-03-24 Updated excel
    [np_swab_results.xlsx]
2020-03-25 we are making adjustments will update the designs w/ what we are sending for testing
    [3mm_2.75cs_0.45d_1.5neck.stl, long bulb test.stl]
2020-03-25 Results: np_swab_results: add Jenny Hu (Seattle) contact info
    [np_swab_results.xlsx]
2020-03-25 updated images and results
    [np_swab_results.xlsx, np_swab_results_03_24_2020.xlsx]
2020-03-25 Updated Results
    [np_swab_results.xlsx, np_swab_results_03_24_2020_2.xlsx]
2020-03-26 Updated results 03_26_2020
    [np_swab_results.xlsx, np_swab_results_03_25_2020_3.xlsx]
2020-03-26 Updating results
    [np_swab_results.xlsx, np_swab_results_03_26_2020_3.xlsx]
